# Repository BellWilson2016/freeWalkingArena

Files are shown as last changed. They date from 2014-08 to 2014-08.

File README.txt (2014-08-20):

Instructions for manufacturing freeWalkingArena1 and LEDdiffuser
JSB 8/2014

These can be laser cut out of plastic, but different thicknesses and types are used for different parts. Quick tip: For plastics that aren't laminated with a protective paper layer, sandwich them between pieces of paper or saran wrap to minimize charring. All scales are in mm. I’ve included AutoCAD DWG, DXF and Adobe Illustrator conversions.

The LEDdiffuser also uses these LED boards: https://github.com/joebell/LEDboard

For plastic I recommend:

1/8” White Acrylic for the diffuser. McMaster #8505K11

3/16" Clear Acrylic for the Floor, Sliders, Slider Stops, and Top Cap. (It's transparent, easy to cut precisely, and easy to tap screw threads into.) McMaster #8560K211 (2 sheets)

1/8" Delrin for the ceiling. (Opaque, chemical resistant.) McMaster #8573K13

1/32" Delrin for the Upper Wall. Good chemical resistance, good thickness. McMaster #8575K131

.020" PETG for the Lower Wall. This layer has the air inlets and outlets to each lane. This is thin enough that flies can't escape out the air inlets, but thick enough to not squish flies when combined with 1/32" Delrin. McMaster #9513K38

Other parts:

You'll want to tap holes for 8-32 thumbscrews in the floor, and 1/4-28 luer lock inlets in the ceiling. A tap handle is also helpful. McMaster #2522A868 #2521A821 #25605A63

8-32 thumbscrews (6 each of two different lengths, 5/16" and 1/2") McMaster #91830A205 #91830A208

Luer fittings and caps. McMaster #51525K23, #51525K37

The LEDdiffuser will require:

	 3 x LEDboards (see https://github.com/joebell/LEDboard)
	12 x 1” 4-40 threaded male-female standoffs McMaster #91075A685	
	12 x 1/4” 4-40 threaded female-female standoffs McMaster #96110A540
	 1 pk x 3/16” 4-40 machine screws McMaster #91772A105
	 1 pk x 4-40 nuts McMaster #90730A005
	 1 pk x 1/4-20 cap screws McMaster #91244A135	
	 1 pk x Rubber bumpers McMaster #8213K1
	1/4-20 tap McMaster #2521A771

Offset the 3 layers of plastic using the 1” standoffs. Attach the LEDboards to the top layer using the 1/4” standoffs. Tap the 1/4” holes for the 1/4-20 cap screws, use these as leveling adjustments with the rubber bumpers. These cap screws should sit directly on top of the central 6 thumbscrews in the behavior arena.

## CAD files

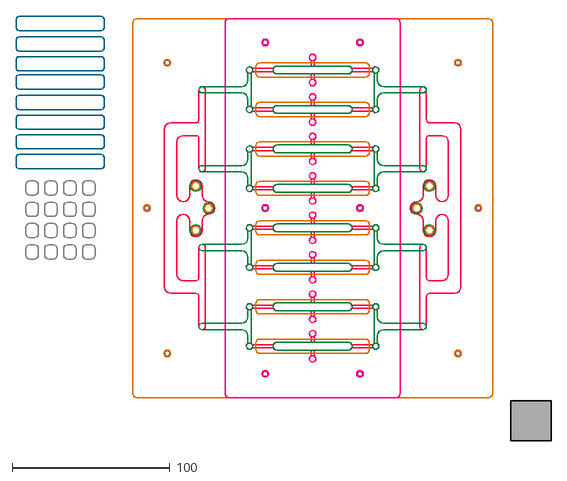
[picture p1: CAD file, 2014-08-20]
freeWalkingArena1.dxf
339.0 x 268.8

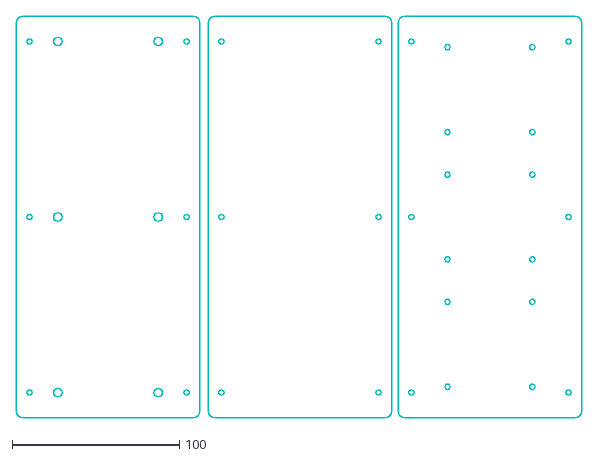
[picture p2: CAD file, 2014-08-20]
LEDdiffuser.dxf
338.5 x 240.0

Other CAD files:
LEDdiffuser.dwg
freeWalkingArena1.dwg
